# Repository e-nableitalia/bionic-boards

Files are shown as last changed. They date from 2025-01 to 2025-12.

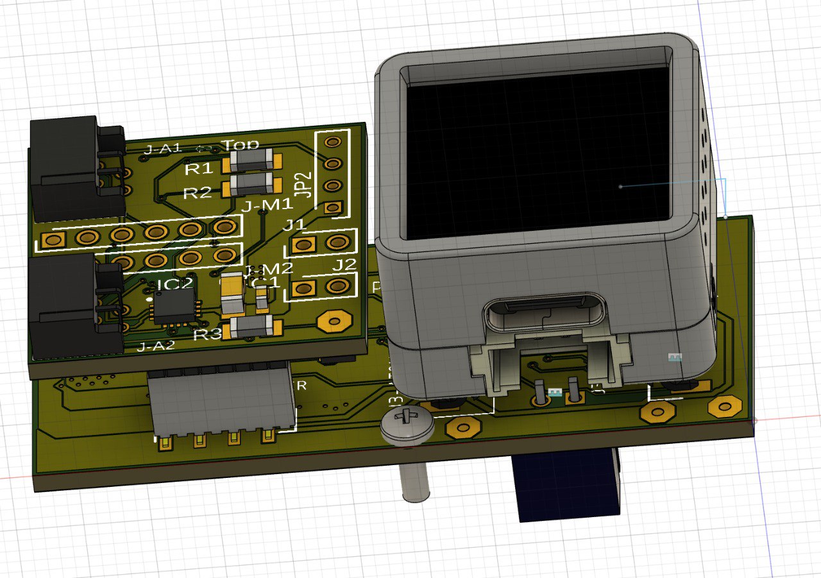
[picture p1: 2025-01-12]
images/Assembly #1.jpeg

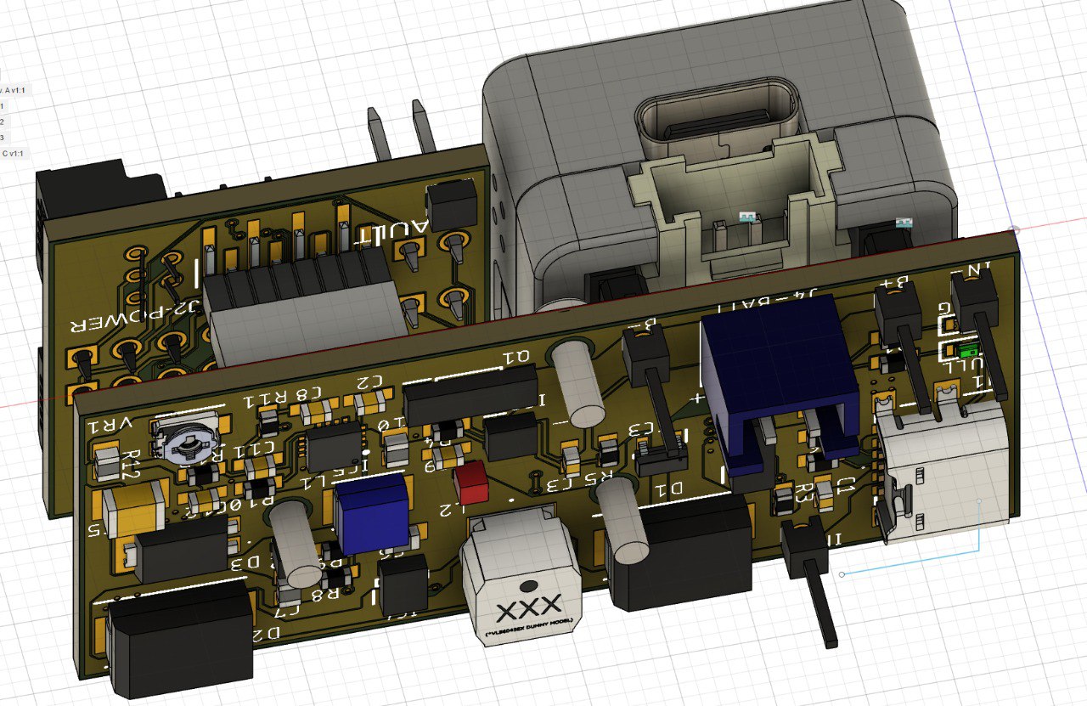
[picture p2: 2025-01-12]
images/Assembly #2.jpeg

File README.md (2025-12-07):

# enable-it Bionic Boards - Third iteration

**This project is part of e-Nable.it Bionic Platform**

An open-source project for developing prosthetic and assistive devices through frugal innovation, designed to be part of e-Nable's open-source prosthetics. The project focuses on building electronic solutions that enable mechanical devices to achieve advanced functionalities, enhancing the community's designs with sophisticated, human-integrated electronic control while maintaining simplicity, affordability, and accessibility.

This project is developed and maintained by the volunteers of the e-Nable Italia community. Our group consists of passionate individuals, including biomedical engineers, mechatronics engineers, and makers, who collaborate to create innovative and accessible solutions. Through our collective efforts, we aim to empower users with open-source, affordable, and customizable assistive devices.

Additional details and information about the **e-nable.it Bionic Platform** can be found in [e-nable.it Bionic Plaform Wiki](https://dev.e-nableitalia.it/wiki/spaces/enableit/pages/360468/Bionic+Workgroup).

# Project roadmap

The project unfolds in three development iterations, each aimed at validating, prototyping, and engineering innovative solutions for low-cost bionic devices.

1. Ideas Validation
The first phase involves conducting experiments and tests to validate initial ideas. This phase focuses on identifying the most promising solutions, exploring various options for controlling actuators and sensors, and collecting data to establish guidelines for the prototype.

2. Prototyping & Custom Solutions
During the prototyping phase, custom solutions are developed using commercial components integrated with specialized electronic boards. The most promising ideas are implemented into physical prototypes to validate architectural and structural concepts. The focus is on simplicity and reliability, ensuring the solutions can be easily replicated and adapted for various bionic devices.

3. Frugal Innovation Engineering
The final phase focuses on engineering the solutions based on frugal innovation principles. Prototypes are optimized to make them accessible, scalable, and practical, with a strong emphasis on cost-effectiveness and real-world applicability. The engineering process also involves creating an open-source hardware platform that enables the creation of modular systems easily combined to build bionic devices.

This repository relates to Iteration #3.

The objective of this iteration is to develop the first reusable deliverables of the project, a set of electronic modules that empower mechanical devices with advanced functionalities. 

By integrating sophisticated, human-centered electronic control, we strive to enhance the capabilities of the e-Nable community's designs while ensuring they remain simple, affordable, and accessible.

> [!CAUTION]
> **The boards published in this repository are still under development and, until fully completed and thoroughly validated, they are intended solely as technological demonstrators and are not designed for practical use.**

## Initial Release Boards

This initial release includes the following boards:

**1. Bionic Controller**  
The Bionic Controller is a custom control board designed to house and expand the capabilities of the M5Stack Atom S3 board. It connects seamlessly to its daughter boards via an 8+8 pin expansion slot.

**This module serves as the foundation for flexible, low-cost prosthetic and assistive device applications.**

Key features:  
- **Size:** 25x50mm  
- **Layers:** 2-layer board  
- **Power Management:** Provides battery management and charging, delivering three power outputs (+3.3V, +5V, and a variable voltage between 5V and 12V for powering multiple motors simultaneously).  
- **Expansion Slot:** Includes a 8+8 pin expansion slot for a daughter board.  
- **Housing:** Designed to house the [M5Stack Atom S3](https://docs.m5stack.com/en/core/AtomS3) board.  

Latest version:
- **Files:** Atom S3 Module Rev. D

**2. ActuatorSense Module**  
The ActuatorSense module is a compact, low-cost H-bridge/waveshare motor controller daughter board designed to connect seamlessly to the expansion slot of the Bionic Controller board.

Key features:  
- **Size:** 26x25mm  
- **Layers:** 2-layer board  
- **Capabilities:**  
  - Can control up to two linear actuators (or two motors).
  - Can control waveshare servo/motors  
  - Supports a combination of one actuator/motor and one sensor (myoelectric or pressure). 

Latest version:
- **Files:** DRV8441A Module Rev B  

**3. Advanced Control Board**  
An enhanced version of the basic control board with added features (not yet released):  
- Includes three slots for daughter boards, enabling control of multiple actuators.  
- Retains all capabilities of the Bionic Controller.  

**4. Daughter Board with TI ADS1298**  
A specialized board for EMG signal acquisition (previous version prototype available):  
- **Functionality:** Designed to acquire up to eight simultaneous myoelectric signals.

## Project updates
250110 - Initial file upload

250113 - Updated to latest release, changes:
- fixed mechanical issue (wrong housing position for Atom S3 board, moved the connectors 4.5 mm below)
- reworked board polygons (cleaner design)
- completed 3d board models
- replaced single pin 2.54 headers with wirepad

250724 - Updated to latest release (DRV8441A Module Rev B), changes:
- tilted pin order on Actuonix PQ12 connector (J-A1 & J-A2 pin order need to be inverted because the connector has contacts on the opposite side)
- added waveshare driver logic and connector (1 wire data + GND + PWR)
- added a digital switch to enable waveshare (default) or additional h-bridge control (2nd motor)
- fixed ADC/Digital Atom S3 pin swap error (G38 & G39 cannot be used as ADC)

## KNOWN ISSUES

- Waveshare connector pinout is tilter: **Pin 1 is connected to Pin 3, and Pin 3 is connected to Pin 1**. Double-check wiring before connecting.

## Authors

Alberto Navatta - alberto@e-nableitalia.it / alberto.navatta@gmail.com

e-Nable Italia - info@e-nableitalia.it

Check for further information, updates and information on this and other e-Nable Italia’s projects on our website: [https://e-nableitalia.it/](https://e-nableitalia.it/)

## License

This material is released under *Creative Commons - Attribution - Non-Commercial - Share Alike license*

## LIMITATION OF LIABILITY.
UNDER NO CIRCUMSTANCES AND UNDER NO LEGAL THEORY, WHETHER TORT (INCLUDING NEGLIGENCE), CONTRACT, OR OTHERWISE, SHALL YOU, THE INITIAL DEVELOPER, ANY OTHER CONTRIBUTOR, OR ANY DISTRIBUTOR OF COVERED CODE, OR ANY SUPPLIER OF ANY OF SUCH PARTIES, BE LIABLE TO ANY PERSON FOR ANY INDIRECT, SPECIAL, INCIDENTAL, OR CONSEQUENTIAL DAMAGES OF ANY CHARACTER INCLUDING, WITHOUT LIMITATION, DAMAGES FOR LOSS OF GOODWILL, WORK STOPPAGE, COMPUTER FAILURE OR MALFUNCTION, OR ANY AND ALL OTHER COMMERCIAL DAMAGES OR LOSSES, EVEN IF SUCH PARTY SHALL HAVE BEEN INFORMED OF THE POSSIBILITY OF SUCH DAMAGES. THIS LIMITATION OF LIABILITY SHALL NOT APPLY TO LIABILITY FOR DEATH OR PERSONAL INJURY RESULTING FROM SUCH PARTY'S NEGLIGENCE TO THE EXTENT APPLICABLE LAW PROHIBITS SUCH LIMITATION. SOME JURISDICTIONS DO NOT ALLOW THE EXCLUSION OR LIMITATION OF INCIDENTAL OR CONSEQUENTIAL DAMAGES, SO THIS EXCLUSION AND LIMITATION MAY NOT APPLY TO YOU.

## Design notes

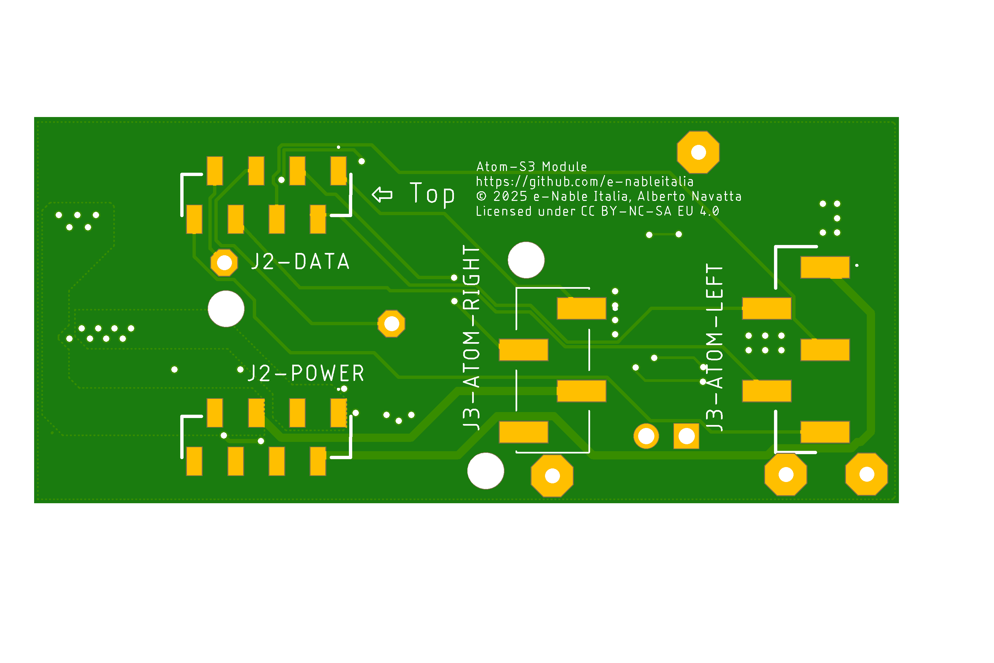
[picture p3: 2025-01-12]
images/Atom S3 Module - Rev. C - Bottom.png

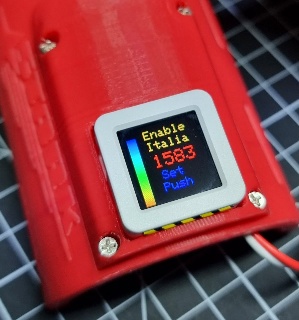
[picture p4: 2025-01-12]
images/Kinetic-With-AtomS3.jpg

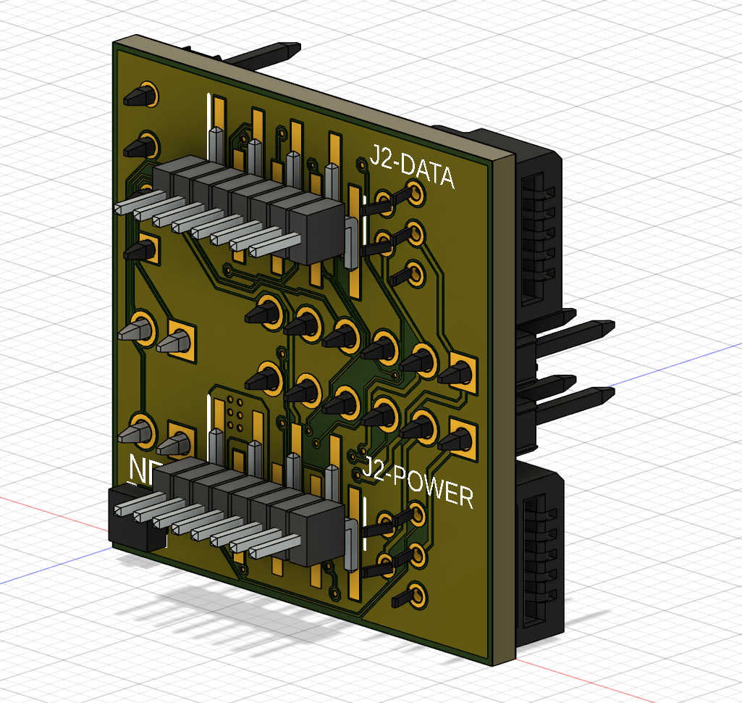
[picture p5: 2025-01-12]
images/DRV8411A Module Rev. A - 3D Top.png

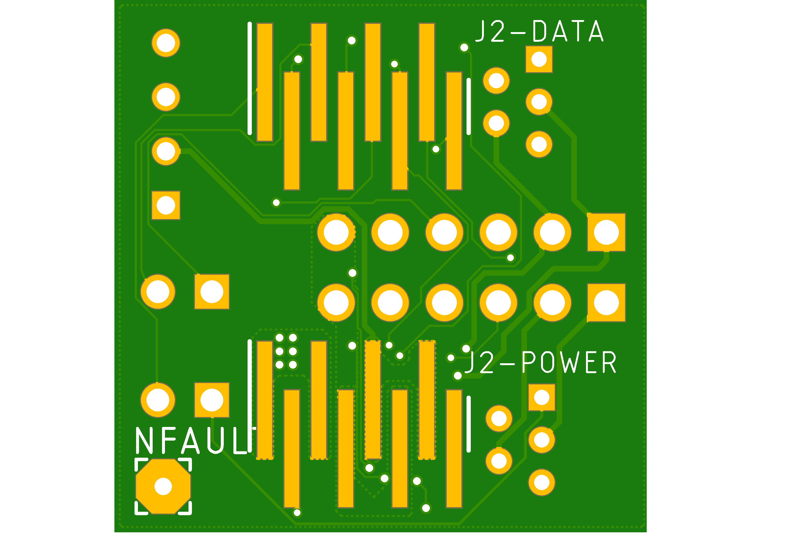
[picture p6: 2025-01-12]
images/DRV8411A Module Rev. A - Top.png

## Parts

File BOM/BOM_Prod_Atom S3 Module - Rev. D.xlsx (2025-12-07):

 |  |  | BOM
Item # | *Designator | *Qty | Manufacturer | *Mfg Part # | Description / Value | *Package/Footprint | Type | Your Instructions / Notes
1 | R3 | 1 | Panasonic | ERJ-U03F1R20V | Thick Film Resistors - SMD 0603 1% 1.2ohm AEC-Q200 Anti-Sulfur | R0603 | SMD
2 | R5 | 1 | Panasonic | ERJ-P03F1000V | Thick Film Resistors - SMD 0603 100ohms 0.2W 1% AEC-Q200 | R0603 | SMD
3 | C1, C3, C9 | 3 | Murata | GCM188R71C104KA37J | Multilayer Ceramic Capacitors MLCC - SMD/SMT 0.1 uF 16 VDC 10% 0603 X7R AEC-Q200 | C0603 | SMD
4 | R13 | 1 | Panasonic | ERJ-3EKF1002V | Thick Film Resistors - SMD 0603 10Kohms 1% AEC-Q200 | R0603 | SMD
5 | C4 | 1 | Murata | GRM188Z71A106KA73D | Multilayer Ceramic Capacitors MLCC - SMD/SMT 10 uF 10 VDC 10% 0603 X7R | C0603 | SMD
6 | R8 | 1 | Panasonic | ERJ-3RED1103V | Thick Film Resistors - SMD 0603 Resistor 0.5% 100ppm 110KOhm | R0603 | SMD
7 | R9 | 1 | Panasonic | ERJ-H3EF1502V | Thick Film Resistors - SMD 0603 15KOhm 1% AEC-Q200 | R0603 | SMD
8 | R1, R2, R4 | 3 | Panasonic | ERJ-U03J102V | Thick Film Resistors - SMD 0603 1Kohms 5% AEC-Q200 | R0603 | SMD
9 | C12 | 1 | Murata | GCJ188R71E105KA01D | Multilayer Ceramic Capacitors MLCC - SMD/SMT 1 uF 25 VDC 10% 0603 X7R AEC-Q200 | C0603 | SMD
10 | C11 | 1 | Murata | GCM188R71H222KA37D | Multilayer Ceramic Capacitors MLCC - SMD/SMT 2200 pF 50 VDC 10% 0603 X7R AEC-Q200 | C0603 | SMD
11 | C2 | 1 | Murata | GCJ188R71E223KA01D | Multilayer Ceramic Capacitors MLCC - SMD/SMT 0.022 uF 25 VDC 10% 0603 X7R AEC-Q200 | C0603 | SMD
12 | C6, C7, C10 | 3 | Murata | GRM21BZ71A226ME15K | Multilayer Ceramic Capacitors MLCC - SMD/SMT 22 uF 10 VDC 20% 0805 X7R | C0805 | SMD
13 | R12 | 1 | YAGEO | RT0805BRD0730K5L | Thin Film Resistors - SMD 1/8W 30.5K Ohms 0.1% | R0805 | SMD
14 | R10 | 1 | Panasonic | ERJ-3EKF3832V | Thick Film Resistors - SMD 0603 38.3Kohms 1% AEC-Q200 | R0603 | SMD
15 | C5 | 1 | Murata | GRM32EC81C476KE15L | Multilayer Ceramic Capacitors MLCC - SMD/SMT 47 uF 16 VDC 10% 1210 X6S | C1210 | SMD
16 | R6, R7 | 2 | Panasonic | ERJ-PA3F5101V | Thick Film Resistors - SMD 0603 5.1Kohm 1% Anti-Surge AEC-Q200 | R0603 | SMD
17 | C8 | 1 | Murata | GCJ188R71E683KA12D | Multilayer Ceramic Capacitors MLCC - SMD/SMT 0.068 uF 25 VDC 10% 0603 X7R AEC-Q200 | C0603 | SMD
18 | J3-ATOM-RIGHT | 1 | Molex | 87898-0466 | Headers & Wire Housings 2.54mm SRSW SMT Hd r W/O Cap 2.5SnL 4P | 878980466 | SMD
19 | J3-ATOM-LEFT | 1 | Molex | 87898-0552 | Headers & Wire Housings 2.54MM SRSW SMT HDR W/CAPT&R .05AULF5P | 878980552 | SMD
20 | R11 | 1 | Vishay / Dale | CRCW0603909RFKEA | Thick Film Resistors - SMD 1/10watt 909ohms 1% | R0603 | SMD
21 | J4-BATT | 1 | JST (JAPAN SOLDERLESS TERMINALS) | B2B-XH-2-TV4(LF)(SN) | Headers & Wire Housings XA HEADER ON RADIAL-TAPE (TOP TYPE) | B2BXH2TV4LFSN | SMD
22 | IC3 | 1 | Diodes Incorporated | DMP1045U-7 | P-Channel Enhancement MOSFET SOT-23 Diodes Inc DMP1045U-7 P-channel MOSFET Transistor, 5.2 A, -12 V, 3-Pin SOT23 | SOT96P240X110-3N | SMD
23 | IC2 | 1 | PJSEMI | DW01A | one cell lithium-ion/polymer battery protection IC | SOT-23-6 | SMD
24 | Q1 | 1 | FUXINSEMI | FS8205A | dual n-channel enhancement mode power MOFSET | SOT-23-6L | SMD
25 | CHRG | 1 | Lite-On | LTST-C191KRKT | Standard LEDs - SMD Red Clear 631nm | LEDC1608X55N | SMD
26 | FULL | 1 | Lite-On | LTST-C193TGKT-5A | Standard LEDs - SMD Green 525nm 90mcd 5mA | LEDC1608X45N | SMD
27 | L1 | 1 | Pulse Electronics | PA4332.222NLT | Inductor Power Shielded Drum Core 2.2uH 20% 1MHz 4.3A 48mOhm DCR 1515 T/R | INDPM4042X200N | SMD
28 | D3 | 1 | Diodes Incorporated | PDS760-13 | Diode Schottky 60V 7A 3Pin PowerDI 5 Diodes Inc PDS760-13, SMT Schottky Diode, 60V 7A, 3-Pin PowerDI 5 | PDS76013 | SMD
29 | J2-DATA, J2-POWER | 2 | SAMTEC | RSM-108-02-L-S | SAMTEC - RSM-108-02-L-S-TR - PCB Receptacle, Board-to-Board, 1.27 mm, 1 Rows, 8 Contacts, Surface Mount, RSM Series | RSM10802LS / SMD,P=1.27mm | SMD
30 | IC4 | 1 | XI'AN Aerosemi Tech | MT3608 | Boost type Adjustable 28V 2A 2V~24V SOT-23-6 DC-DC Converters ROHS | SOT-23-6 | SMD
31 | D1, D2 | 2 | onsemi | SS34 | ON Semi SS34 SMT Schottky Diode, 40V 3A, 2-Pin DO-214AB | DIOM8059X256N | SMD
32 | VR1 | 1 | Bourns | TC33X-2-503E | Trimmer Resistors - SMD 3MM 50KOHMS 25% 0.1WATT OPEN FRM | TC33X2304E | SMD
33 | IC1 | 1 | TOP POWER | TP4056-42-ESOP8 | 1A Standalone Linear Li-lon Battery Charger with Thermal | ESOP-8 | SMD
34 | IC5 | 1 | Texas Instruments | TPS55340RTER | TEXAS INSTRUMENTS - TPS55340RTER - DC/DC CONV, BOOST/SEPIC/FLYBACK, WQFN-16 | QFN50P300X300X80-17N | SMD
35 | J1 | 1 | GCT (GLOBAL CONNECTOR TECHNOLOGY) | USB4135-GF-A | USB Connectors USBC Rec GF RA 6P SMT-SMT stakes 3.16mm | USB4135GFA | SMD
36 | L2 | 1 | TDK | VLS6045AF-220M | SMD / SMT Inductors (Coils), L=22?H, L x W x T : | SMD,6x6mm | SMD
37 | G1, G2 | 2 |  | WIREPAD1,6/0,9 | Wire PAD connect wire on PCB | 1,6/0,9 | DNS
38 | B+, B-, IN+, IN- | 4 |  | WIREPAD2,54/0,9 | Wire PAD connect wire on PCB | 2,54/0,9 | DNS
Need a quick and accurante quote? Need an efficient production? Please read SMT Ordering Necessary Files & Info in 1 minute. Thank you very much! (https://www.pcbway.com/smt_ordering_guide.html)
Click for Instructions on How to Create a BOM (https://www.pcbway.com/blog/PCB_Assembly/How_to_Build_a_BOM__Bill_Of_Materials_.html)

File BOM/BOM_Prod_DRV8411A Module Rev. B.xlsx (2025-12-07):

 |  |  | BOM
Item # | *Designator | *Qty | Manufacturer | *Mfg Part # | Description / Value | *Package/Footprint | Type | Your Instructions / Notes
1 | C1, C3, C4 | 3 | Murata | GCJ188R71H104KA12D | Multilayer Ceramic Capacitors MLCC - SMD/SMT 0.1 uF 50 VDC 10% 0603 X7R AEC-Q200 | C0603 | SMD
2 | R1, R2, R3, R4, R5, R6, R7, R8 | 8 | Panasonic | ERJ-P08F1002V | Thick Film Resistors - SMD 1206 10Kohms 0.66W 1% AEC-Q200 | R1206 | SMD
3 | C2 | 1 | Murata | GRM31CR71E106KA12L | Multilayer Ceramic Capacitors MLCC - SMD/SMT 10 uF 25 VDC 10% 1206 X7R | C1206 | SMD
4 | R9 | 1 | Panasonic | ERJ-P08F2002V | Thick Film Resistors - SMD 1206 20Kohms 0.66W 1% AEC-Q200 | R1206 | SMD
5 | J3-WAVE | 1 | Molex | 22-05-7035 | Headers & Wire Housings 3 CKT 2.5MM R/A HDR | SHDRRA3W60P0X250_1X3_990X790X4 | thru-hole
6 | J-M1, J-M2 | 2 | Molex | 22-28-4063 | Headers & Wire Housings BREAKAWAY HDR VERT 6 | HDRV6W66P0X254_1X6_1524X249X83 | thru-hole
7 | IC1 | 1 | Nexperia | 74HC4053D,653 | Multiplexer Switch ICs MULTIPLEXER SWITCH ICS | SOIC127P600X175-16N | SMD
8 | IC2 | 1 | Texas Instruments | DRV8411ARTER | Motor / Motion / Ignition Controllers & Drivers 1.65-V to 11-V, 4-A dual H-bridge motor driver with IPROPI current regulation | QFN50P300X300X80-17N | SMD
9 | J2-DATA, J2-POWER | 2 | Harwin | M50-3630842 | 1.27mm (0.05") Pitch SIL Vertical SMT Pin Header, selective gold + tin, 8 contacts | HUSRSP8W42P127_1016X210X430P | SMD
10 | Q1 | 1 | Micro Commercial Components (MCC) | MMSS8550HE3-L-TP | Bipolar Transistors - BJT Vcbo -40V -25Vceo Vebo -6V 1.5A 625mW | SOT95P237X125-3N | SMD
11 | J-A1, J-A2 | 2 | Molex | 52807-0510 | FFC & FPC Connectors 1.00 MM R/A FFC/FPC 5 Circuit Non-ZIF | MOLEX_52807-0510_0 | thru-hole
12 | IC4 | 1 | Texas Instruments | SN74LVC1G125DBVR | Buffers & Line Drivers SINGLE BUS BUFFER GA TE A 595-SN74LVC1G125DBVT | SOT95P280X145-5N | SMD
13 | IC3 | 1 | Texas Instruments | SN74LVC1G126DBVR | Buffers & Line Drivers Single Bus Buffer A 595-SN74LVC1G126DBVT | SOT95P280X145-5N | SMD
14
15
16
17
18
19 |  | 1
20
21
22
23
24
25
26
27
28
29
30
31
32
33
34
35
36
37
38
39
40
41
42
43
Need a quick and accurante quote? Need an efficient production? Please read SMT Ordering Necessary Files & Info in 1 minute. Thank you very much! (https://www.pcbway.com/smt_ordering_guide.html)
Click for Instructions on How to Create a BOM (https://www.pcbway.com/blog/PCB_Assembly/How_to_Build_a_BOM__Bill_Of_Materials_.html)

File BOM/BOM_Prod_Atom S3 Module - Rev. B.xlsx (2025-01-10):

 |  |  | BOM
Item # | *Designator | *Qty | Manufacturer | *Mfg Part # | Description / Value | *Package/Footprint | Type | Your Instructions / Notes
1 | R3 | 1 | Panasonic | ERJ-U03F1R20V | Thick Film Resistors - SMD 0603 1% 1.2ohm AEC-Q200 Anti-Sulfur | R0603 | SMD
2 | R5 | 1 | Panasonic | ERJ-P03F1000V | Thick Film Resistors - SMD 0603 100ohms 0.2W 1% AEC-Q200 | R0603 | SMD
3 | C1, C3, C9 | 3 | Murata | GCM188R71C104KA37J | Multilayer Ceramic Capacitors MLCC - SMD/SMT 0.1 uF 16 VDC 10% 0603 X7R AEC-Q200 | C0603 | SMD
4 | R13 | 1 | Panasonic | ERJ-3EKF1002V | Thick Film Resistors - SMD 0603 10Kohms 1% AEC-Q200 | R0603 | SMD
5 | C4 | 1 | Murata | GRM188Z71A106KA73D | Multilayer Ceramic Capacitors MLCC - SMD/SMT 10 uF 10 VDC 10% 0603 X7R | C0603 | SMD
6 | R8 | 1 | Panasonic | ERJ-3RED1103V | Thick Film Resistors - SMD 0603 Resistor 0.5% 100ppm 110KOhm | R0603 | SMD
7 | R9 | 1 | Panasonic | ERJ-H3EF1502V | Thick Film Resistors - SMD 0603 15KOhm 1% AEC-Q200 | R0603 | SMD
8 | R1, R2, R4 | 3 | Panasonic | ERJ-U03J102V | Thick Film Resistors - SMD 0603 1Kohms 1% AEC-Q200 | R0603 | SMD
9 | C12 | 1 | Murata | GCJ188R71E105KA01D | Multilayer Ceramic Capacitors MLCC - SMD/SMT 1 uF 25 VDC 10% 0603 X7R AEC-Q200 | C0603 | SMD
10 | C11 | 1 | Murata | GCM188R71H222KA37D | Multilayer Ceramic Capacitors MLCC - SMD/SMT 2200 pF 50 VDC 10% 0603 X7R AEC-Q200 | C0603 | SMD
11 | C2 | 1 | Murata | GCJ188R71E223KA01D | Multilayer Ceramic Capacitors MLCC - SMD/SMT 0.022 uF 25 VDC 10% 0603 X7R AEC-Q200 | C0603 | SMD
12 | C6, C7, C10 | 3 | Murata | GRM21BZ71A226ME15K | Multilayer Ceramic Capacitors MLCC - SMD/SMT 22 uF 10 VDC 20% 0805 X7R | C0805 | SMD
13 | R12 | 1 | YAGEO | RT0805BRD0730K5L | Thin Film Resistors - SMD 1/8W 30.5K Ohms 0.1% | R0805 | SMD
14 | R10 | 1 | Panasonic | ERJ-3EKF3832V | Thick Film Resistors - SMD 0603 38.3Kohms 1% AEC-Q200 | R0603 | SMD
15 | C5 | 1 | Murata | GRM32EC81C476KE15L | Multilayer Ceramic Capacitors MLCC - SMD/SMT 47 uF 16 VDC 10% 1210 X6S | C1206 | SMD
16 | B+, B-, IN+, IN- | 4 | TE Connectivity | 5-146281-1 | Headers & Wire Housings HDR VT 1X01P .1" 230/110 30AU | 51462811 | SMD
17 | R6, R7 | 2 | Panasonic | ERJ-PA3F5101V | Thick Film Resistors - SMD 0603 5.1Kohm 1% Anti-Surge AEC-Q200 | R0603 | SMD
18 | C8 | 1 | Murata | GCJ188R71E683KA12D | Multilayer Ceramic Capacitors MLCC - SMD/SMT 0.068 uF 25 VDC 10% 0603 X7R AEC-Q200 | C0603 | SMD
19 | J3-ATOM-RIGHT | 1 | Molex | 87898-0466 | Headers & Wire Housings 2.54mm SRSW SMT Hd r W/O Cap 2.5SnL 4P | 878980466 | SMD
20 | J3-ATOM-LEFT | 1 | Molex | 87898-0552 | Headers & Wire Housings 2.54MM SRSW SMT HDR W/CAPT&R .05AULF5P | 878980552 | SMD
21 | R11 | 1 | Vishay / Dale | CRCW0603909RFKEA | Thick Film Resistors - SMD 1/10watt 909ohms 1% | R0603 | SMD
22 | J4-BATT | 1 | JST (JAPAN SOLDERLESS TERMINALS) | B2B-XH-2-TV4(LF)(SN) | Headers & Wire Housings XA HEADER ON RADIAL-TAPE (TOP TYPE) | B2BXH2TV4LFSN | SMD
23 | IC3 | 1 | Diodes Incorporated | DMP1045U-7 | P-Channel Enhancement MOSFET SOT-23 Diodes Inc DMP1045U-7 P-channel MOSFET Transistor, 5.2 A, -12 V, 3-Pin SOT23 | SOT96P240X110-3N | SMD
24 | IC2 | 1 | SII Semiconductor | DW01A-G | one cell lithium-ion/polymer battery protection IC | SOT95P190X145-6N | SMD
25 | Q1 | 1 | SII Semiconductor | FS8205A | dual n-channel enhancement mode power MOFSET | SOP65P640X120-8N | SMD
26 | CHRG | 1 | Lite-On | LTST-C191KRKT | Standard LEDs - SMD Red Clear 631nm | LEDC1608X55N | SMD
27 | FULL | 1 | Lite-On | LTST-C193TGKT-5A | Standard LEDs - SMD Green 525nm 90mcd 5mA | LEDC1608X45N | SMD
28 | L1 | 1 | Pulse Electronics | PA4332.222NLT | Inductor Power Shielded Drum Core 2.2uH 20% 1MHz 4.3A 48mOhm DCR 1515 T/R | INDPM4042X200N | SMD
29 | D3 | 1 | Diodes Incorporated | PDS760-13 | Diode Schottky 60V 7A 3Pin PowerDI 5 Diodes Inc PDS760-13, SMT Schottky Diode, 60V 7A, 3-Pin PowerDI 5 | PDS76013 | SMD
30 | J2-DATA, J2-POWER | 2 | SAMTEC | RSM-108-02-L-S-TR | SAMTEC - RSM-108-02-L-S-TR - PCB Receptacle, Board-to-Board, 1.27 mm, 1 Rows, 8 Contacts, Surface Mount, RSM Series | RSM10802LSTR | SMD
31 | IC4 | 1 | Olimex Ltd. | SMD IC MT3608 | Switching Voltage Regulators | SOT95P280X145-6N | SMD
32 | D1, D2 | 2 | onsemi | SS34 | ON Semi SS34 SMT Schottky Diode, 40V 3A, 2-Pin DO-214AB | DIOM8059X256N | SMD
33 | VR1 | 1 | Bourns | TC33X-2-503E | Trimmer Resistors - SMD 3MM 50KOHMS 25% 0.1WATT OPEN FRM | TC33X2304E | SMD
34 | IC1 | 1 | TOP POWER | TP4056-EMSOP8 | 1A Standalone Linear Li-lon Battery Charger with Thermal | SOP65P490X110-9N | SMD
35 | IC5 | 1 | Texas Instruments | TPS55340RTER | TEXAS INSTRUMENTS - TPS55340RTER - DC/DC CONV, BOOST/SEPIC/FLYBACK, WQFN-16 | QFN50P300X300X80-17N | SMD
36 | J1 | 1 | GCT (GLOBAL CONNECTOR TECHNOLOGY) | USB4135-GF-A | USB Connectors USBC Rec GF RA 6P SMT-SMT stakes 3.16mm | USB4135GFA | SMD
37 | L2 | 1 | TDK | VLS6045AF-220M | SMD / SMT Inductors (Coils), L=22?H, L x W x T : | VLS6045 | SMD
38 | G1, G2 | 2 |  | WIREPAD1,6/0,9 | Wire PAD connect wire on PCB | 1,6/0,9 | DNS
Need a quick and accurante quote? Need an efficient production? Please read SMT Ordering Necessary Files & Info in 1 minute. Thank you very much! (https://www.pcbway.com/smt_ordering_guide.html)
Click for Instructions on How to Create a BOM (https://www.pcbway.com/blog/PCB_Assembly/How_to_Build_a_BOM__Bill_Of_Materials_.html)

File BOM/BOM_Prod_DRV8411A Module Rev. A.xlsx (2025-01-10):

 |  |  | BOM
Item # | *Designator | *Qty | Manufacturer | *Mfg Part # | Description / Value | *Package/Footprint | Type | Your Instructions / Notes
1 | C1 | 1 | Murata | GCJ188R71H104KA12D | Multilayer Ceramic Capacitors MLCC - SMD/SMT 0.1 uF 50 VDC 10% 0603 X7R AEC-Q200 | C0603 | SMD
2 | R1, R2, R3 | 3 | Panasonic | ERJ-P08F1002V | Thick Film Resistors - SMD 1206 10Kohms 0.66W 1% AEC-Q200 | R1206 | SMD
3 | C2 | 1 | Murata | GRM31CR71E106KA12L | Multilayer Ceramic Capacitors MLCC - SMD/SMT 10 uF 25 VDC 10% 1206 X7R | C1206 | SMD
4 | J1, J2 | 2 | Molex | 22-28-4023 | Molex KK 254 42375, 2.54mm Pitch, 2 Way, 1 Row Unshrouded, Straight Pin Header, Through Hole, Solder Termination | HDRV2W87P0X254_1X2_508X249X863 | thru-hole
5 | JP2 | 1 | Molex | 22-28-4046 | Headers & Wire Housings 2.54MM HDR VT 4P 240/125 30AU | HDRV4W66P0X254_1X4_1016X249X83 | thru-hole
6 | J-M1, J-M2 | 2 | Molex | 22-28-4063 | Headers & Wire Housings BREAKAWAY HDR VERT 6 | HDRV6W66P0X254_1X6_1524X249X83 | thru-hole
7 | IC2 | 1 | Texas Instruments | DRV8411ARTER | Motor / Motion / Ignition Controllers & Drivers 1.65-V to 11-V, 4-A dual H-bridge motor driver with IPROPI current regulation | QFN50P300X300X80-17N | SMD
8 | J2-DATA, J2-POWER | 2 | SAMTEC | FTR-108-03-S-S | CONN HEADER SMD 8 POS 1.27MM | HUSRSP8W46P127_1016X248X572P | SMD
9 | J-A1, J-A2 | 2 | Molex | 52807-0510 | FFC & FPC Connectors 1.00 MM R/A FFC/FPC 5 Circuit Non-ZIF | MOLEX_52807-0510_0 | thru-hole
10 | NFAULT | 1 |  | WIREPAD2,54/0,8 | Wire PAD connect wire on PCB | 2,54/0,8 | DNS
11
12
13
14
15
16
17
18
19
20
21
22
23
24
25
26
27
28
29
30
31
32
33
34
Need a quick and accurante quote? Need an efficient production? Please read SMT Ordering Necessary Files & Info in 1 minute. Thank you very much! (https://www.pcbway.com/smt_ordering_guide.html)
Click for Instructions on How to Create a BOM (https://www.pcbway.com/blog/PCB_Assembly/How_to_Build_a_BOM__Bill_Of_Materials_.html)

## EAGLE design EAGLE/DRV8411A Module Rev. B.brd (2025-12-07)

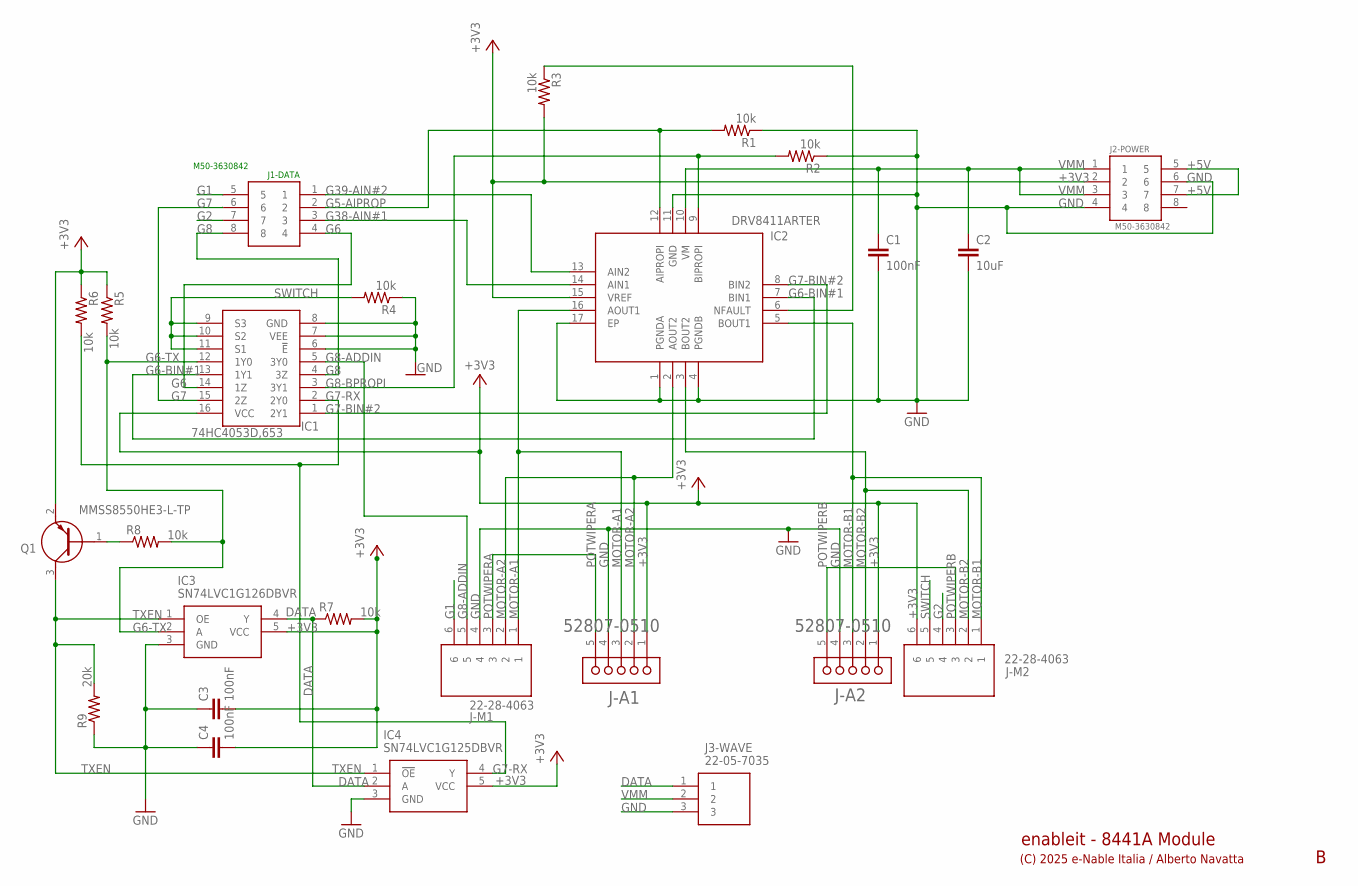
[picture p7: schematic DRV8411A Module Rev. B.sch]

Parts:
C1, C3, C4: 100nF; C0603
C2: 10uF; C1206
IC1: 74HC4053D,653; SOIC127P600X175-16N
IC2: DRV8411ARTER; QFN50P300X300X80-17N
IC3: SN74LVC1G126DBVR; SOT95P280X145-5N
IC4: SN74LVC1G125DBVR; SOT95P280X145-5N
J1-DATA, J2-POWER: M50-3630842; HUSRSP8W42P127_1016X210X430P
J3-WAVE: 22-05-7035; SHDRRA3W60P0X250_1X3_990X790X4
J-A1, J-A2: MOLEX_52807-0510MOLEX_52807-0510_0_0; MOLEX_52807-0510_0
J-M1, J-M2: 22-28-4063; HDRV6W66P0X254_1X6_1524X249X83
Q1: MMSS8550HE3-L-TP; SOT95P237X125-3N
R1, R2, R3, R4, R5, R6, R7, R8: 10k; R1206
R9: 20k; R1206

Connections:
+3V3: C3.2, C4.2, IC1.16 (VCC), IC2.15 (VREF), IC3.5 (VCC), IC4.5 (VCC), J2-POWER.2, J-A1.1, J-A2.1, J-M2.6, Q1.2 (E), R3.2, R5.1, R6.1, R7.2
+5V: J2-POWER.5, J2-POWER.7
DATA: IC3.4 (Y), IC4.2 (A), J3-WAVE.1, R7.1
G1: J1-DATA.5, J-M1.6
G2: J1-DATA.7, J-M2.4
G5-AIPROP: IC2.12 (AIPROPI), J1-DATA.2, R1.2
G6: IC1.14 (1Z), J1-DATA.4
G6-BIN#1: IC1.13 (1Y1), IC2.7 (BIN1)
G6-TX: IC1.12 (1Y0), IC3.2 (A), R5.2, R8.2
G7: IC1.15 (2Z), J1-DATA.6
G7-BIN#2: IC1.1 (2Y1), IC2.8 (BIN2)
G7-RX: IC1.2 (2Y0), IC4.4 (Y), R6.2
G8: IC1.4 (3Z), J1-DATA.8
G8-ADDIN: IC1.5 (3Y0), J-M1.5
G8-BPROPI: IC1.3 (3Y1), IC2.9 (BIPROPI), R2.2
G38-AIN#1: IC2.14 (AIN1), J1-DATA.3
G39-AIN#2: IC2.13 (AIN2), J1-DATA.1
GND: C1.2, C2.2, C3.1, C4.1, IC1.6 (!E), IC1.7 (VEE), IC1.8 (GND), IC2.1 (PGNDA), IC2.4 (PGNDB), IC2.11 (GND), IC2.17 (EP), IC3.3 (GND), IC4.3 (GND), J2-POWER.4, J2-POWER.6, J3-WAVE.3, J-A1.4, J-A2.4, J-M1.4, R1.1, R2.1, R4.1, R9.1
MOTOR-A1: IC2.16 (AOUT1), J-A1.3, J-M1.1
MOTOR-A2: IC2.2 (AOUT2), J-A1.2, J-M1.2
MOTOR-B1: IC2.5 (BOUT1), J-A2.3, J-M2.1
MOTOR-B2: IC2.3 (BOUT2), J-A2.2, J-M2.2
unnamed: Q1.1 (B), R8.1
NFAULT: IC2.6 (NFAULT), R3.1
POTWIPERA: J-A1.5, J-M1.3
POTWIPERB: J-A2.5, J-M2.3
SWITCH: IC1.9 (S3), IC1.10 (S2), IC1.11 (S1), J-M2.5, R4.2
TXEN: IC3.1 (OE), IC4.1 (!OE), Q1.3 (C), R9.2
VMM: C1.1, C2.1, IC2.10 (VM), J2-POWER.1, J2-POWER.3, J3-WAVE.2

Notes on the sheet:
(C) 2025 e-Nable Italia / Alberto Navatta
enableit - 8441A Module

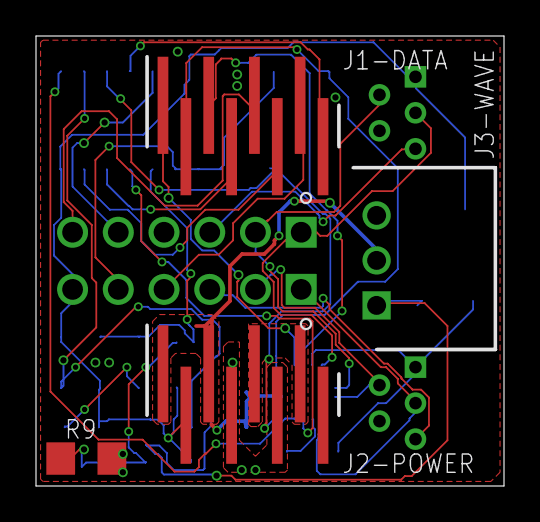
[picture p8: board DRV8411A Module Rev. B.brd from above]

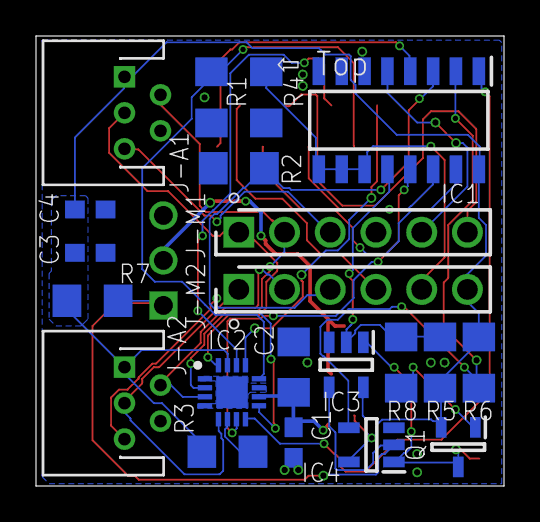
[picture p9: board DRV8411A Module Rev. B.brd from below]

Board: 2 copper layers, 26.0 x 25.0 mm, 25 parts (21 on the bottom side), 29 nets.

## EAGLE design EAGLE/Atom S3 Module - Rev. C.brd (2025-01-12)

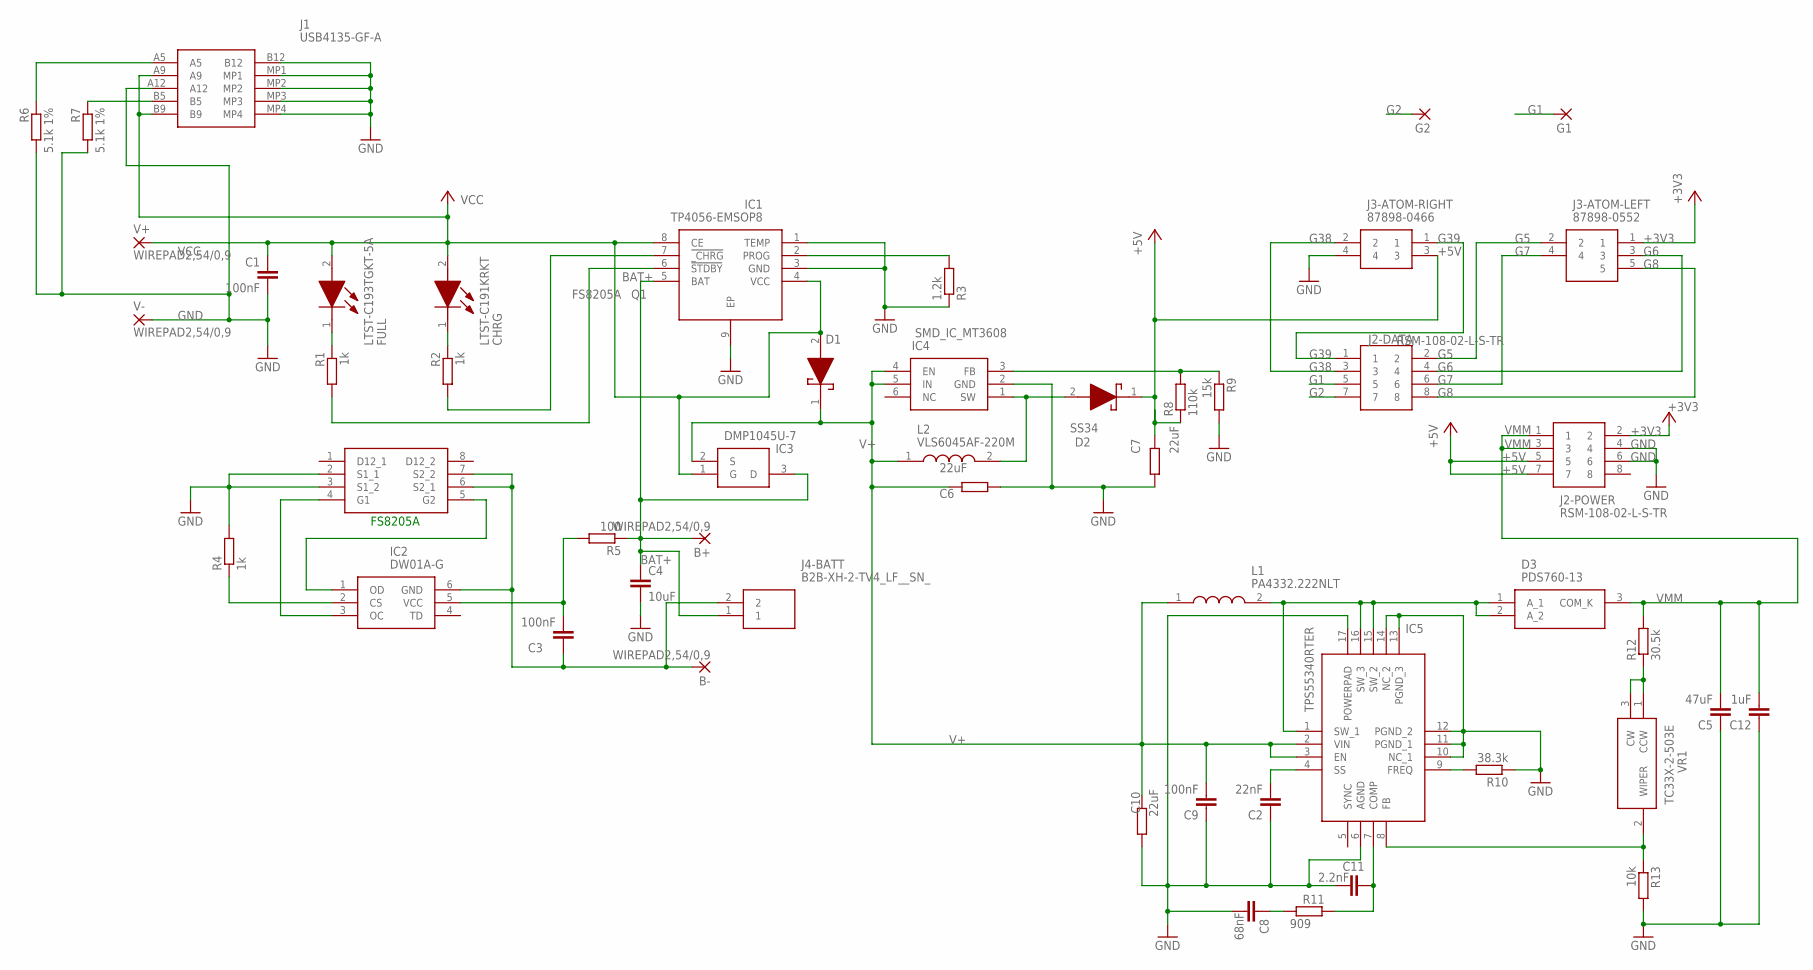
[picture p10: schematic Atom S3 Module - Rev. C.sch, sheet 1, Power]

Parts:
B+: WIREPAD2,54/0,9; 2,54/0,9
B-: WIREPAD2,54/0,9; 2,54/0,9
C1, C3, C9: 100nF; C0603
C2: 22nF; C0603
C4: 10uF; C0603
C5: 47uF; C1210
C6, C7, C10: 22uF; R0805
C8: 68nF; C0603
C11: 2.2nF; C0603
C12: 1uF; C0603
CHRG: LTST-C191KRKT; LEDC1608X55N
D1, D2: SS34; DIOM8059X256N
D3: PDS760-13; PDS76013
FULL: LTST-C193TGKT-5A; LEDC1608X45N
G1, G2: WIREPAD1,6/0,9; 1,6/0,9
IC1: TP4056-EMSOP8; SOP65P490X110-9N
IC2: DW01A-G; SOT95P190X145-6N
IC3: DMP1045U-7; SOT96P240X110-3N
IC4: SMD_IC_MT3608; SOT95P280X145-6N
IC5: TPS55340RTER; QFN50P300X300X80-17N
J1: USB4135-GF-A; USB4135GFA
J2-DATA, J2-POWER: RSM-108-02-L-S-TR; RSM10802LSTR
J3-ATOM-LEFT: 87898-0552; 878980552
J3-ATOM-RIGHT: 87898-0466; 878980466
J4-BATT: B2B-XH-2-TV4_LF__SN_; B2BXH2TV4LFSN
L1: PA4332.222NLT; INDPM4042X200N
L2: VLS6045AF-220M; VLS6045
Q1: FS8205A; SOP65P640X120-8N
R1, R2, R4: 1k; R0603
R3: 1.2k; R0603
R5: 100; R0603
R6, R7: 5.1k 1%; R0603
R8: 110k; R0603
R9: 15k; R0603
R10: 38.3k; R0603
R11: 909; R0603
R12: 30.5k; R0805
R13: 10k; R0603
V+: WIREPAD2,54/0,9; 2,54/0,9
V-: WIREPAD2,54/0,9; 2,54/0,9
VR1: TC33X-2-503E; TC33X2503E

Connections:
+3V3: J2-POWER.2, J3-ATOM-LEFT.1
+5V: C7.2, D2.1 (K), J2-POWER.5, J2-POWER.7, J3-ATOM-RIGHT.3, R8.1
BAT+: B+.1, C4.1, IC1.5 (BAT), IC3.3 (D), J4-BATT.1, R5.1
BAT-: B-.1, C3.1, IC2.6 (GND), J4-BATT.2, Q1.6 (S2_1), Q1.7 (S2_2)
G1: G1.1, J2-DATA.5
G2: G2.1, J2-DATA.7
G5: J2-DATA.2, J3-ATOM-LEFT.2
G6: J2-DATA.4, J3-ATOM-LEFT.3
G7: J2-DATA.6, J3-ATOM-LEFT.4
G8: J2-DATA.8, J3-ATOM-LEFT.5
G38: J2-DATA.3, J3-ATOM-RIGHT.2
G39: J2-DATA.1, J3-ATOM-RIGHT.1
GND: C1.2, C2.1, C4.2, C5.1, C6.1, C7.1, C8.2, C9.1, C10.1, C11.2, C12.1, IC1.1 (TEMP), IC1.3 (GND), IC1.9 (EP), IC4.2 (GND), IC5.6 (AGND), IC5.10 (NC_1), IC5.11 (PGND_1), IC5.12 (PGND_2), IC5.13 (PGND_3), IC5.14 (NC_2), IC5.17 (POWERPAD), J1.A12, J1.B12, J1.MP1, J1.MP2, J1.MP3, J1.MP4, J2-POWER.4, J2-POWER.6, J3-ATOM-RIGHT.4, Q1.2 (S1_1), Q1.3 (S1_2), R3.1, R4.2, R6.2, R7.2, R9.2, R10.1, R13.2, V-.1
unnamed: FULL.1 (K), R1.1
unnamed: CHRG.1 (K), R2.1
unnamed: IC1.6 (!STDBY), R1.2
unnamed: IC1.7 (!_CHRG), R2.2
unnamed: IC2.3 (OC), Q1.4 (G1)
unnamed: J1.B5, R7.1
unnamed: IC1.2 (PROG), R3.2
unnamed: IC2.2 (CS), R4.1
unnamed: IC2.1 (OD), Q1.5 (G2)
unnamed: D2.2 (A), IC4.1 (SW), L2.2
unnamed: C3.2, IC2.5 (VCC), R5.2
unnamed: J1.A5, R6.1
unnamed: IC5.9 (FREQ), R10.2
unnamed: IC4.3 (FB), R8.2, R9.1
unnamed: C11.1, IC5.7 (COMP), R11.2
unnamed: C8.1, R11.1
unnamed: D3.1 (A_1), D3.2 (A_2), IC5.1 (SW_1), IC5.15 (SW_2), IC5.16 (SW_3), L1.2
unnamed: C2.2, IC5.4 (SS)
unnamed: R12.1, VR1.1 (CCW), VR1.3 (CW)
unnamed: IC5.8 (FB), R13.1, VR1.2 (WIPER)
V+: C6.2, C9.2, C10.2, D1.1 (K), IC3.2 (S), IC4.4 (EN), IC4.5 (IN), IC5.2 (VIN), IC5.3 (EN), L1.1, L2.1
VCC: C1.1, CHRG.2 (A), D1.2 (A), FULL.2 (A), IC1.4 (VCC), IC1.8 (CE), IC3.1 (G), J1.A9, J1.B9, V+.1
VMM: C5.2, C12.2, D3.3 (COM_K), J2-POWER.1, J2-POWER.3, R12.2

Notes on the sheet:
FS8205A

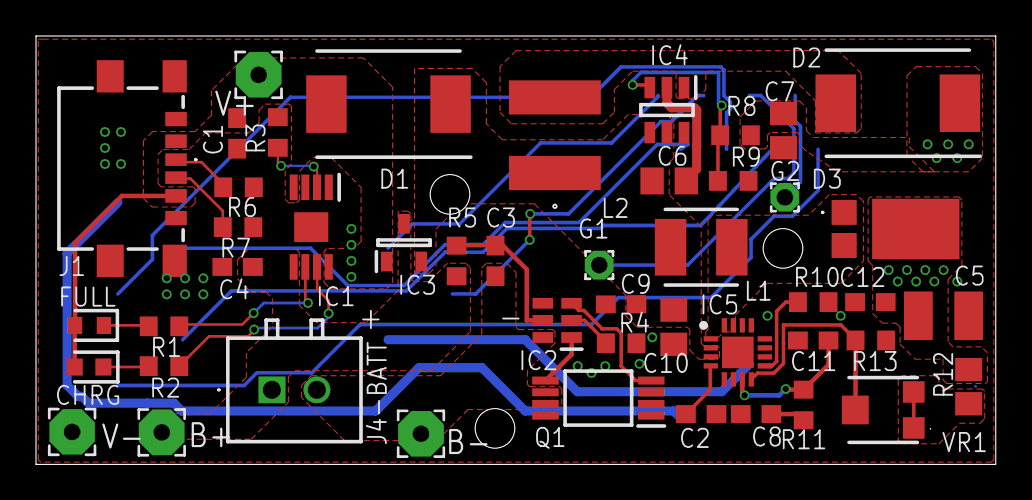
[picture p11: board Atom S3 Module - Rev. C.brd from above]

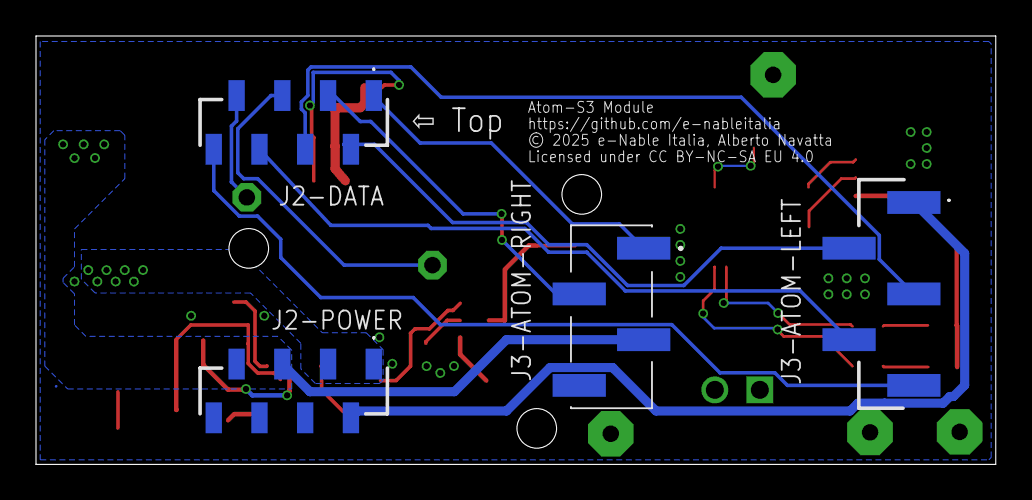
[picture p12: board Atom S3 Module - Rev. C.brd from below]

Board: 2 copper layers, 53.3 x 23.8 mm, 51 parts (4 on the bottom side), 36 nets.

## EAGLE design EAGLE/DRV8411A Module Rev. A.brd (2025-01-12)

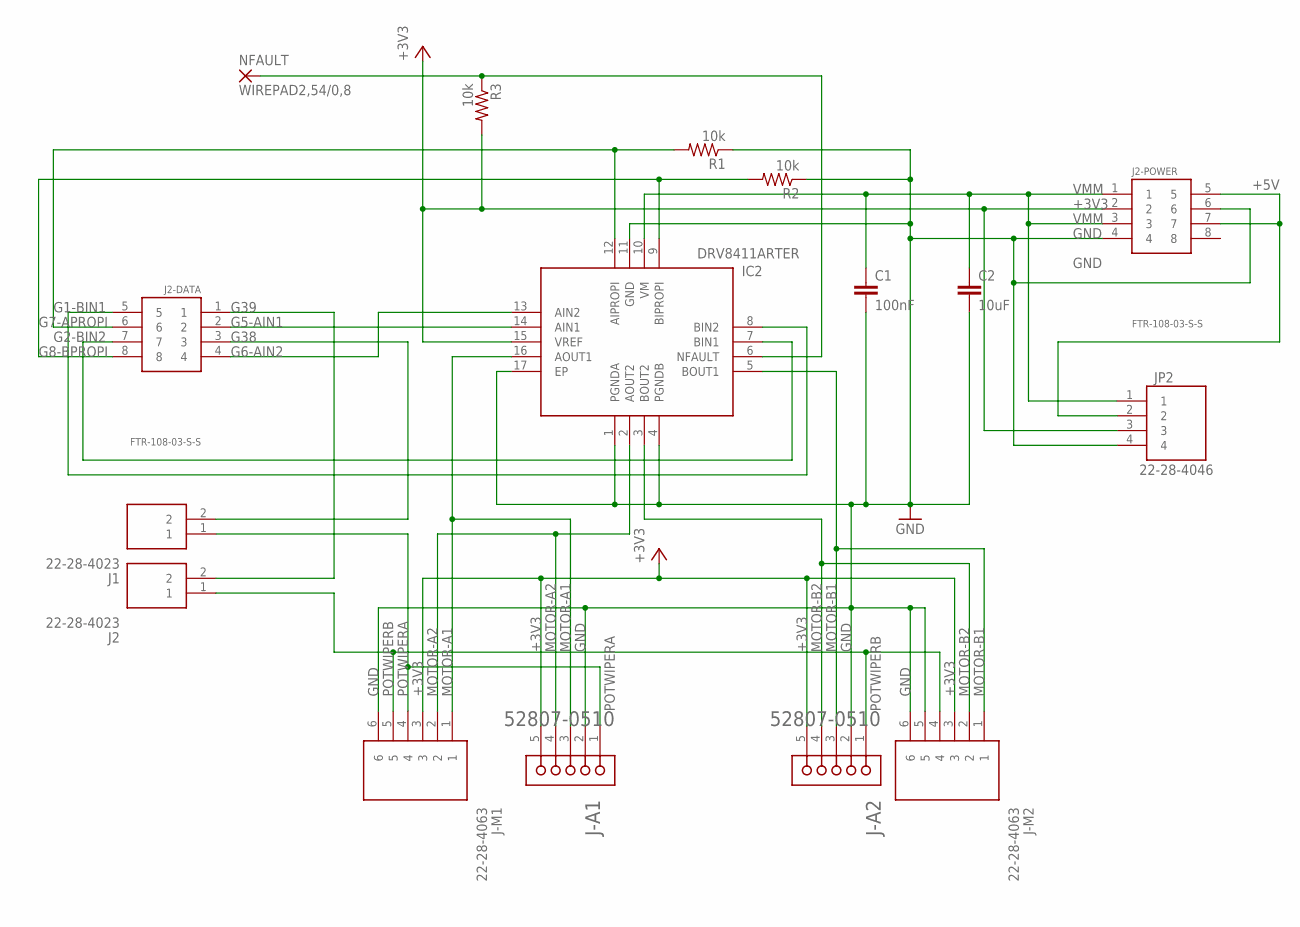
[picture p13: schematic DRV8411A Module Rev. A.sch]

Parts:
C1: 100nF; C0603
C2: 10uF; C1206
IC2: DRV8411ARTER; QFN50P300X300X80-17N
J1, J2: 22-28-4023; HDRV2W87P0X254_1X2_508X249X863
J2-DATA, J2-POWER: FTR-108-03-S-S; HUSRSP8W46P127_1016X248X572P
J-A1, J-A2: MOLEX_52807-0510MOLEX_52807-0510_0_0; MOLEX_52807-0510_0
J-M1, J-M2: 22-28-4063; HDRV6W66P0X254_1X6_1524X249X83
JP2: 22-28-4046; HDRV4W66P0X254_1X4_1016X249X83
NFAULT: WIREPAD2,54/0,8; 2,54/0,8
R1, R2, R3: 10k; R1206

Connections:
+3V3: IC2.15 (VREF), J2-POWER.2, J-A1.5, J-A2.5, J-M1.3, J-M2.3, JP2.3, R3.2
+5V: J2-POWER.5, J2-POWER.7, JP2.2
G1-BIN1: IC2.8 (BIN2), J2-DATA.5
G2-BIN2: IC2.7 (BIN1), J2-DATA.7
G5-AIN1: IC2.14 (AIN1), J2-DATA.2
G6-AIN2: IC2.13 (AIN2), J2-DATA.4
G7-APROPI: IC2.12 (AIPROPI), J2-DATA.6, R1.2
G8-BPROPI: IC2.9 (BIPROPI), J2-DATA.8, R2.2
G38: J1.2, J2-DATA.3
G39: J2.2, J2-DATA.1
GND: C1.2, C2.2, IC2.1 (PGNDA), IC2.4 (PGNDB), IC2.11 (GND), IC2.17 (EP), J2-POWER.4, J2-POWER.6, J-A1.2, J-A2.2, J-M1.6, J-M2.5, J-M2.6, JP2.4, R1.1, R2.1
MOTOR-A1: IC2.16 (AOUT1), J-A1.3, J-M1.1
MOTOR-A2: IC2.2 (AOUT2), J-A1.4, J-M1.2
MOTOR-B1: IC2.5 (BOUT1), J-A2.3, J-M2.1
MOTOR-B2: IC2.3 (BOUT2), J-A2.4, J-M2.2
NFAULT: IC2.6 (NFAULT), NFAULT.1, R3.1
POTWIPERA: J1.1, J-A1.1, J-M1.4
POTWIPERB: J2.1, J-A2.1, J-M1.5, J-M2.4
VMM: C1.1, C2.1, IC2.10 (VM), J2-POWER.1, J2-POWER.3, JP2.1

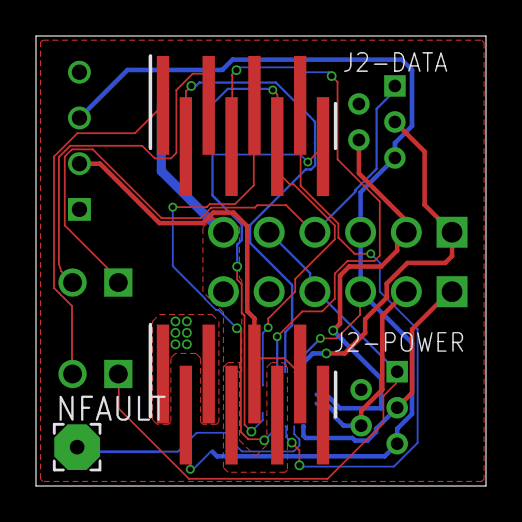
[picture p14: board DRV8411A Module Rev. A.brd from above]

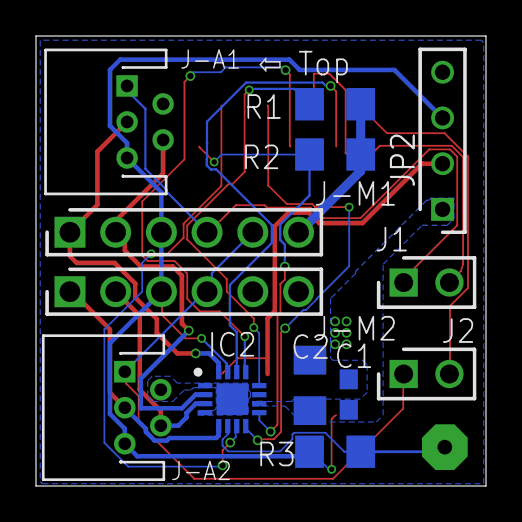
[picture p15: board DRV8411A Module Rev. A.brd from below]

Board: 2 copper layers, 25.0 x 25.0 mm, 16 parts (13 on the bottom side), 19 nets.

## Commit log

2025-01-10 added first release of BOM, eagle projects and gerber files
    [Atom S3 Module - Rev. B.brd, Atom S3 Module - Rev. B.sch, BOM_Prod_Atom S3 Module - Rev. B.xlsx, BOM_Prod_DRV8411A Module Rev. A.xlsx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]
2025-01-12 updated to the latest version, fixed mechanical design to adjust housing of Atom S3 board, added holes for secure mounting
    [Atom S3 Module - Rev. C.brd, Atom S3 Module - Rev. C.sch, BOM_Prod_Atom S3 Module - Rev. C.xlsx, DRV8411A Module Rev. A.brd]
2025-12-07 Update README.md with latest module revisions and features
    - Updated Atom S3 Module to Rev. D
    - Enhanced ActuatorSense module description and updated size
    - Revised latest version of ActuatorSense to Rev. B
    - Clarified features of Advanced Control Board and Daughter Board with TI ADS1298
    - Added new project update for DRV8441A Module Rev B with detailed changes
    - Fixed minor formatting issues and updated contact information
    [BOM_Prod_Atom S3 Module - Rev. D.xlsx, BOM_Prod_DRV8411A Module Rev. B.xlsx, DRV8411A Module Rev. B.brd, DRV8411A Module Rev. B.sch]
2025-12-07 Update README.md to clarify known issues with Waveshare connector pinout

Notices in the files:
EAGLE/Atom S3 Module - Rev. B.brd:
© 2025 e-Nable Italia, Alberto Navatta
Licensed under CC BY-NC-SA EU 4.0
